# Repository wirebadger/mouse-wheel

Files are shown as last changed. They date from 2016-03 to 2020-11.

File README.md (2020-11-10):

# mouse-wheel
Arduino based exercise wheel counter for mice

# Overview
We want to see how much exercise a mouse is doing so want to count the number of revolutions on the mouse wheel.  We don't care which way the wheel is turning or how fast. In principle this is quite a simple revolution counter.

# Prototype
## Design

A magnet is glued under the wheel and every time it passes over a hall effect sensor it generates a pulse which is counted by connecting it to one of the external interrupt pins on the Arduino board.  This simple arrangement generates a lot of noisy triggers when the wheel rests with the magnet just over the sensor.  To avoid them, a second magnet is glued 180 degrees further round the wheel and a second hall effect sensor (B) is placed at 90 degrees.  Each time a magnet passes a sensor we switch to looking at the other sensor.  Every 1/4 revolution the wheel generates a signal from one of the sensors and every half turn passes sensor A and increments the count.  We are actually counting half revolutions so the result is scaled by two before display.

## Build

Glue two magnets 180 degrees apart on the wheel section.  It matters which way up they go as the sensors only detect one magnetic polarity.  

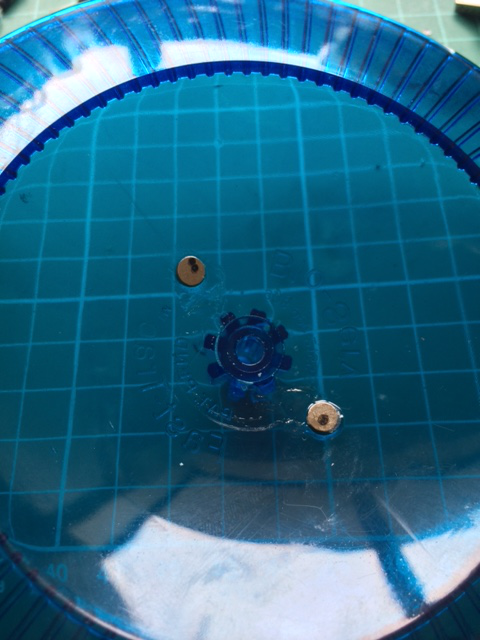
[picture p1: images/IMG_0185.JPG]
Wheel with magnets


In terms of assembly, the wheel is made of special mouse safe plastic but the rest of the wires and electronics need to be safe too.  The simplest way to get a circular PCB right up close to the wheel was to canibalise the encoder board from a small motor from [deal extreme](http://www.dx.com/p/high-torque-25mm-dc-12-0v-330rpm-encoder-precision-gear-motor-418535). 

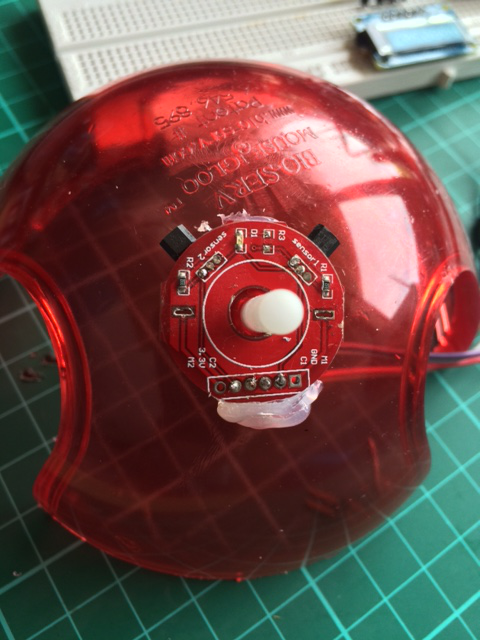
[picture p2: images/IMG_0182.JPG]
Encoder circuit


Carefully lever off the round magnet from the motor, desolder the motor pins and remove the PCB assembly. Remove the right angle connector and swap the hall effect sensors to the back  of the PCB or else the PCB doesn't fit between the wheel and the housing. Solder dupont terminated wires from the reverse side of the PCB to terminals GND, C1, C2 and VCC.  Note that this module is (probably) 3V3.  Also remove R3, the LED's resistor just to disconnect the LED and save power.  No need for disco lights.

The rest of the electronics will be housed in an aluminium enclosure and battery powered for safety. The cables running between the sensors and enclosure need to be sheathed in steel braid.

## Breadboard version
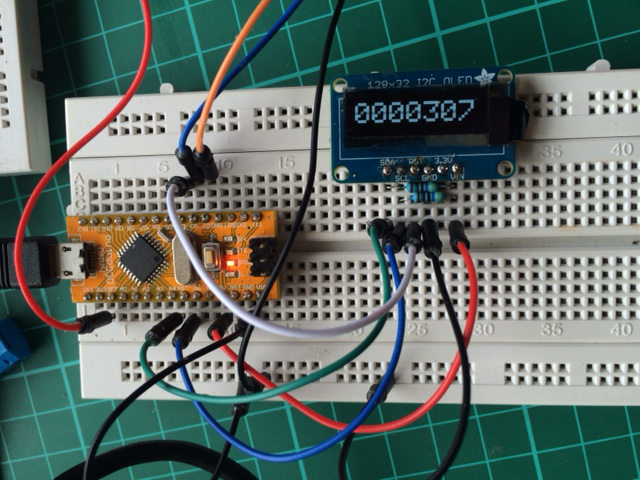
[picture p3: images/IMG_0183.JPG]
Electronics


# Results

The waveform from the two hall effect sensors can be seen below.

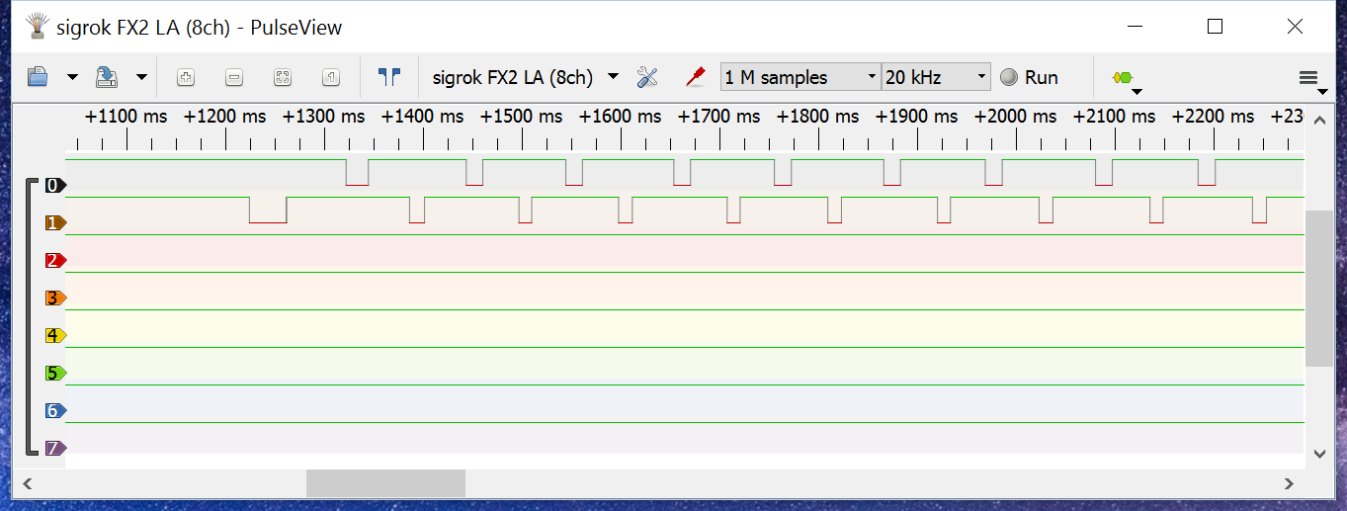
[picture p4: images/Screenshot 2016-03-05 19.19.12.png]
Outputs from both Hall Effect sensors


A falling edge on the top trace is counted only after there has been a falling edge on the second trace (brown).

If the wheel happens to stop over one of the sensors a noisy trace is generated but the addtional transitions are not counted as there is no activity on the second channel.

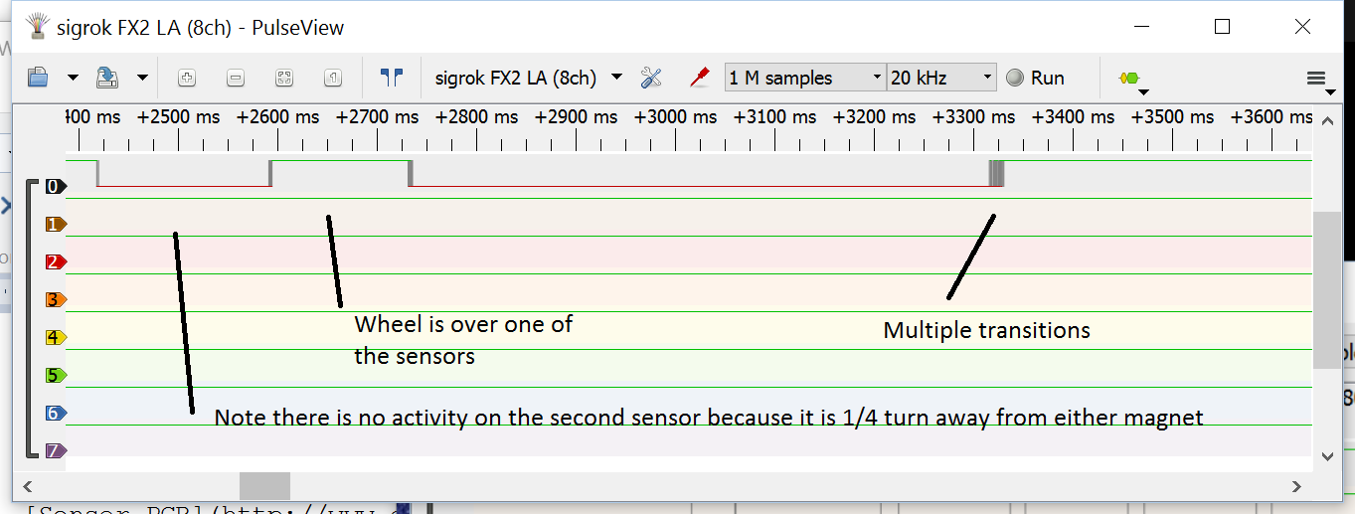
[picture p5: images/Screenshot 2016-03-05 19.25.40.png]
Wheel stops over one sensor


# First Production Build

Pro Mini connections:

|Name | Pin |Function                  |
|-----|-----|--------------------------|
|D2|5| Hall Effect sensor C1 |
|D3|6| Hall Effect sensor C2     |
|D4|7| Display Reset (active low) |
|D8|11| Wake up switch with 100k pullup to Vcc| 
|A4|-| SDA I2C line (pulled up to  Vcc with 4K7 resistor) |
|A5|-| SCL I2C line (pulled up to  Vcc with 4K7 resistor) |
|A0|17| mid point of Vraw resistor divider (2x100k) |
|Vraw|24| Unregulated supply|
|3V3|21| Supply to sensor and display|
|GND|4| Common ground |
|RXD|2| Pull high with 100k |

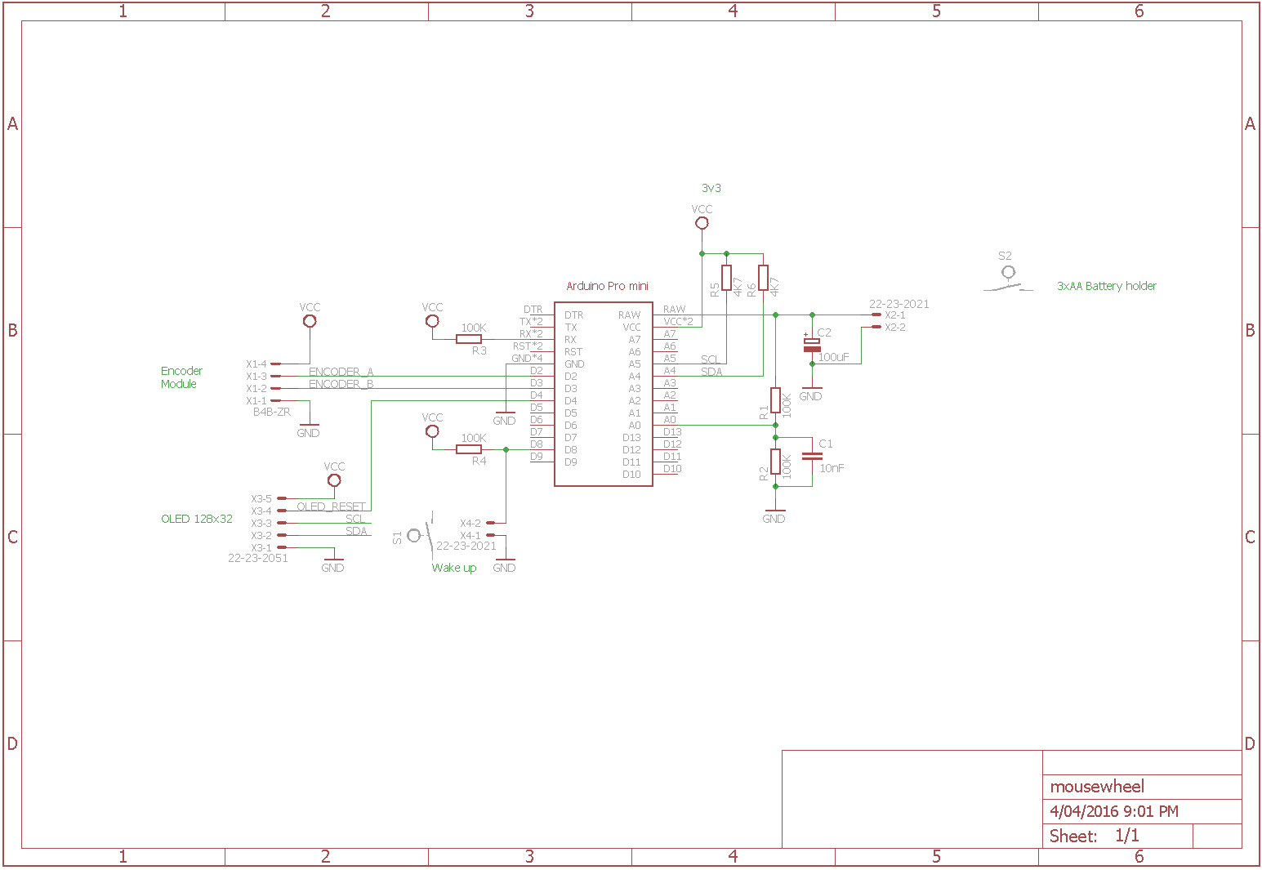
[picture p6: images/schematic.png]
Schematic


The display is the AdaFruit OLED 128x32 I2C module

## Components
### Hardware
[Display Module](https://www.adafruit.com/products/931) Adafruit OLED display

[Sensor PCB](http://www.dx.com/p/high-torque-25mm-dc-12-0v-330rpm-encoder-precision-gear-motor-418535) Removed from Motor

Was  
[Nano DCCDuino](http://www.dx.com/p/new-nano-v3-0-module-atmega328p-au-improved-version-for-arduino-yellow-369070) Set Arduino IDE for Arduino Nano

Now  
Pro Mini
Remove the LED resistor on the Pro Mini to save current

| Condition  |Ibatt typ|
|------------|---------|
|Display On  | 20mA    |
|Display Off | 4mA     |
 
### Libraries
Requires the following libraries:
* Adafruit_GFX
* Adafruit_SSD1306
* Pin Change Interrupt

Just install them using the library manager.

# Main production

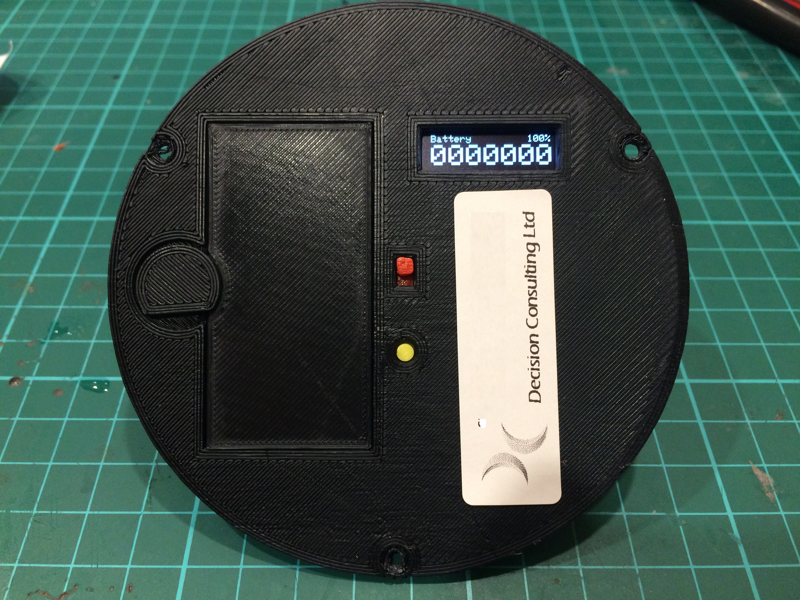
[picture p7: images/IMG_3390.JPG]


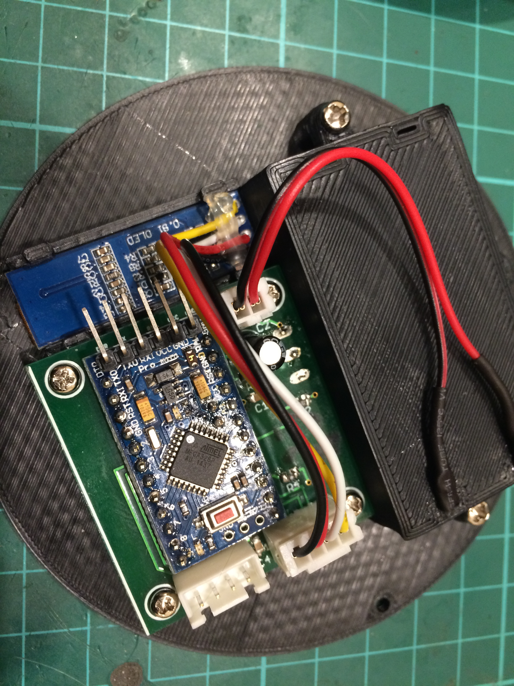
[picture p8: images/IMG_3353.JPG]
Internals


## 3D printed mechanics

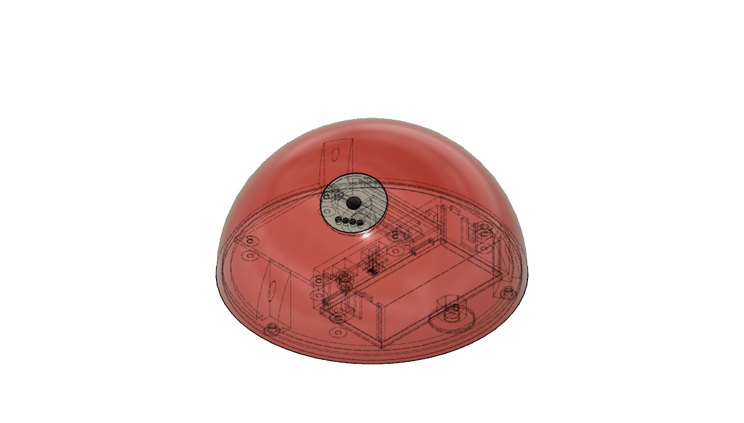
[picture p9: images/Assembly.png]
Assembly


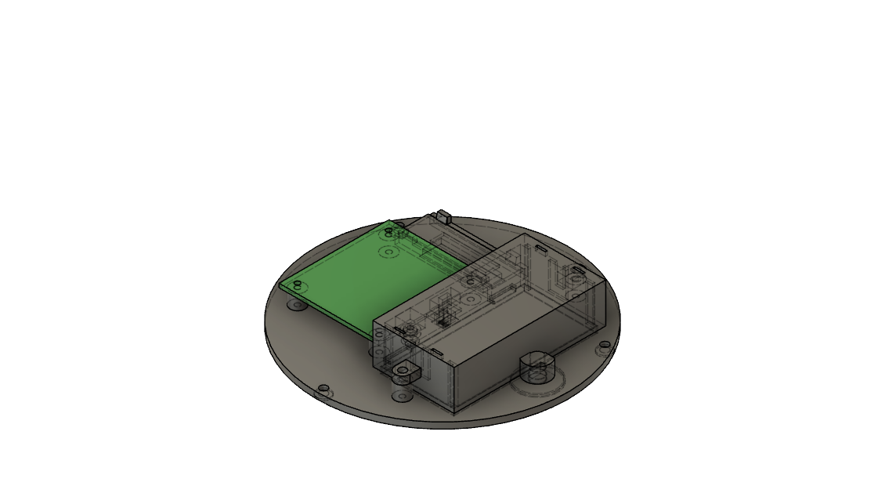
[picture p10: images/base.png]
Base


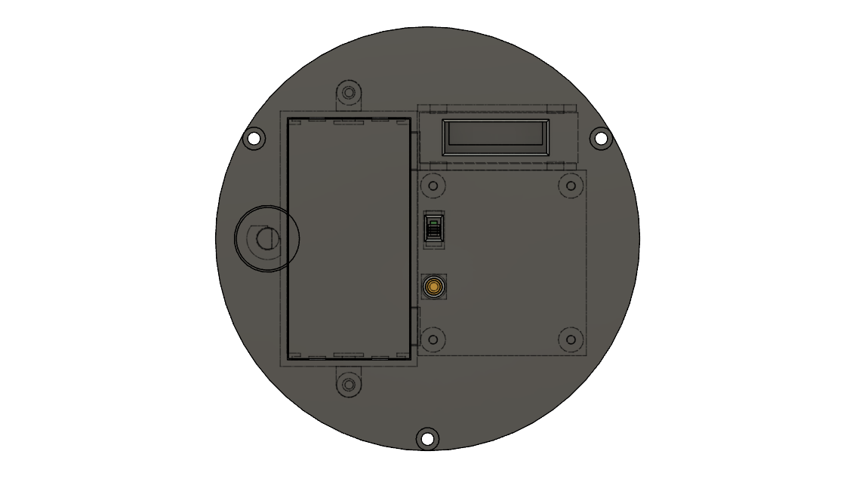
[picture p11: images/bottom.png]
Underside


See mechanical directory for design files

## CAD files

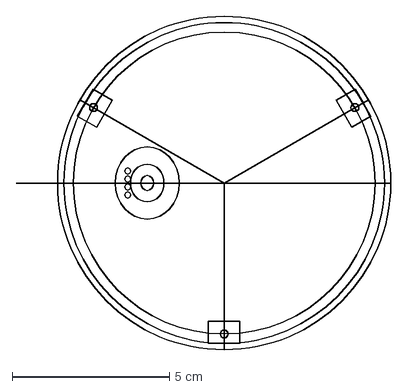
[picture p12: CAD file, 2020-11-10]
mechanical/Dome v2.dxf
11.9 x 10.6 cm

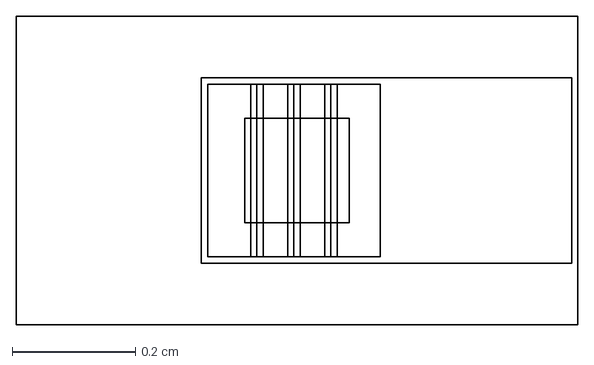
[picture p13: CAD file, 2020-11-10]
mechanical/switch.dxf
0.91 x 0.5 cm

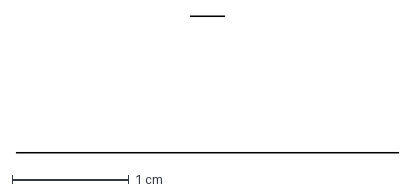
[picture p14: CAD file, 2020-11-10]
mechanical/Battery_Case_AA.dxf
3.28 x 1.17 cm

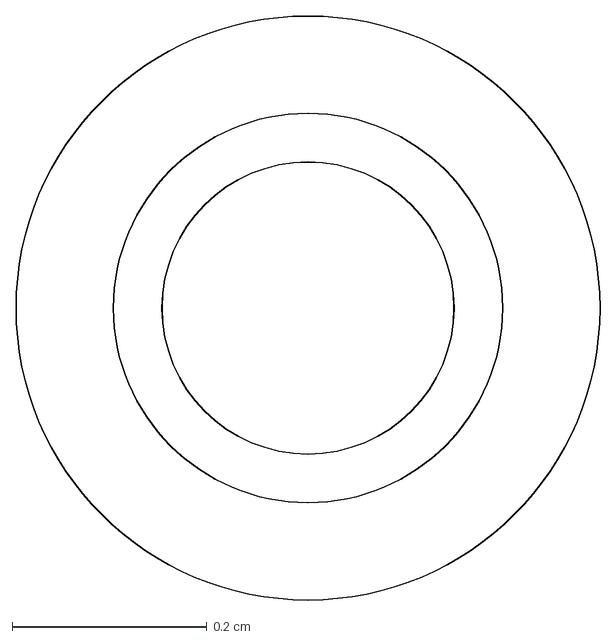
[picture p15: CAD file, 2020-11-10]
mechanical/Button.dxf
0.6 x 0.6 cm

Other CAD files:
mechanical/Assembly AA.dxf
mechanical/AA Lid.dxf
mechanical/Latch.dxf
mechanical/PCB.dxf
mechanical/Lock.dxf
mechanical/Display.dxf
mechanical/Base_AA.dxf
mechanical/Sensor PCB.dxf

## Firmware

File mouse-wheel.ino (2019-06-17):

/*! -----------------------------------------------------------------------
 * Mouse exerise wheel counter
 * Copyright [2016] Andy Dachs
 *
 * Licensed under the Apache License, Version 2.0 (the "License");
 * you may not use this file except in compliance with the License.
 * You may obtain a copy of the License at
 *
 *   http://www.apache.org/licenses/LICENSE-2.0
 *
 * Unless required by applicable law or agreed to in writing, software
 * distributed under the License is distributed on an "AS IS" BASIS,
 * WITHOUT WARRANTIES OR CONDITIONS OF ANY KIND, either express or implied.
 * See the License for the specific language governing permissions and
 * limitations under the License.
 * 
 * ------------------------------------------------------------------------
 * 
 * We want to see how exercise our mouse is doing so want to count the number of revolutions
 * on his mouse wheel.  We don't care which way the wheel is turning or how fast.
 * In principle this is quite a simple revolution counter.
 * 
 * A magnet is glued under the wheel and every time it passes over a hall effect sensor (A) it
 * generates a pulse which we can count by connecting it on of the external interrupt pins on the 
 * Arduino board.  This simple arrangement generates a lot of noisy triggers when the wheel rests 
 * with the magnet just over the sensor.  To avoid them, a second magnet is glued 180 degrees 
 * further round the wheel.  A second hall effect sensor (B) is placed at 90 degrees.  Each time 
 * a magnet passes a sensor we switch to looking at the other sensor.  Every 1/4 revolution the 
 * wheel generates a signal from one of the sensors and every half turn passes sensor A and 
 * increments the count.  We are actually counting half revolutions so the result is scaled by 
 * two before display.
 * 
 * The display is the AdaFruit OLED 128x32 I2C module
 * 
 * Requires the Adafruit_GFX and Adafruit_SSD1306. Just install them using the library manager.
 * 
 * Author: Andy Dachs
 * Date:   5th March 2016
 * 
 */

// uncomment one of these
// #define LITHIUM_1S
#define ALKALINE_2AA

// uncomment one of these
//#define LCD_128_64       // 128x64 display, i2c address 0x78/0x3C first 5 units
#define LCD_128_32       // 128x32 display, i2c address 0x78/0x3C
//#define LCD_96_16        // 0.9" narrow OLED


#include <Wire.h>
#include <Adafruit_GFX.h>
#include <Adafruit_SSD1306.h>
#include <avr/sleep.h>
#include <PinChangeInterrupt.h>


#define ENCODER_A  2          // hall effect sensor A
#define ENCODER_B  3          // quadrature hall effect sensor B
#define OLED_RESET 4          // reset pin for display module
#define WAKE_UP_SWITCH 8    // switch to wake up display
#define PIN_VBATT      A0


#ifdef LCD_96_16
#define LCDADDR     0x3C
#define LCDWIDTH    96
#define LCDHEIGHT   16 
#elif defined(LCD_128_32)
#define LCDADDR     0x3C
#define LCDWIDTH    128
#define LCDHEIGHT   32  
#elif defined(LCD_128_64)
#define LCDADDR     0x3C
#define LCDWIDTH    128
#define LCDHEIGHT   64 
#else
#error No display defined
#endif
/* Different units have different values of the resistor divider. The intention was to run from 3V but now also
 * allow for 3v7.
 * R2 47K, sometimes two in parallel 
 * R1 100K, change to 150K for LiOn
 */
#define R2                        47      //k ohms
#define R1                        150     //k ohms
#define VREF                      1100    // mV internal reference

#define VOLTAGE_SCALE             (unsigned long)(((R1+R2)*(unsigned long)VREF)/(R2))
#define VOLTAGE_HYSTERISIS        3       // mV

#ifdef ALKALINE_2AA
/* From http://www.powerstream.com/AA-tests.htm */
/* an AA battery is full at 1.45V, fully discharged at 1.1v*/
#define VBATT_FULL               (1450UL*2)   // times number of cells (below 1.45 too non-linear)
//#define VBATT_EMPTY              (1200UL*2)   // the limit is the TLE4913 hall effect Vmin 2.4V
#define VBATT_EMPTY              (1100UL*2)   // TSH253CX operates down to 1v8 so 1.1V/cell is the limit 
#define CAPACITY                 (2000UL)     // mAh
#elif defined(LITHIUM_1S)
#define VBATT_FULL               (3700UL)   
#define VBATT_EMPTY              (2900UL)    // 
#define CAPACITY                 (2600UL)    // mAh
#else
#error No Battery chemistry defined
#endif

#define REMAINING_PERCENT(mV)            ((((mV)-VBATT_EMPTY)*100)/(VBATT_FULL-VBATT_EMPTY))


#define MAX_COUNT (unsigned long)10000000

#define SERIAL_OUTPUT 1

#define DISPLAY_TIME_OUT      10000    // display timeout in ms
#define DISPLAY_REFRESH_TIME  250       // refresh display at this rate

/*! These variables must be declared volatile because they
 * are modifed in the interrupt handlers. If the main loop
 * needs to access them, interrupts must be disabled.
 */
volatile unsigned int encoder0Pos = 0;
volatile unsigned long revCount;
volatile boolean expectA;
volatile boolean displayIsActive = true;


Adafruit_SSD1306 display(LCDWIDTH, LCDHEIGHT, &Wire); //deprecated constructor display(OLED_RESET);

void doEncoderA(void);
void doEncoderB(void);
void wakeUp(void );



void setup() 
{
  pinMode(ENCODER_A, INPUT_PULLUP); 
  pinMode(ENCODER_B, INPUT_PULLUP); 

  pinMode( WAKE_UP_SWITCH, INPUT_PULLUP );
  digitalWrite( WAKE_UP_SWITCH, HIGH );

  pinMode(PIN_VBATT, INPUT);
  
  expectA = true;
  revCount = 0;

  /* Initialise OLED */
  display.begin(SSD1306_SWITCHCAPVCC, LCDADDR);  // initialize with the I2C addr
  display.clearDisplay();                            // Clear the buffer.
  display.dim(true);
    
  // encoder pin on interrupt 0 (pin 2)
  attachInterrupt(digitalPinToInterrupt(ENCODER_A), doEncoderA, FALLING);

  // encoder pin on interrupt 1 (pin 3)
  attachInterrupt(digitalPinToInterrupt(ENCODER_B), doEncoderB, FALLING);

  attachPinChangeInterrupt(digitalPinToPinChangeInterrupt(WAKE_UP_SWITCH), wakeUp, FALLING );

  disablePinChangeInterrupt(digitalPinToPinChangeInterrupt(WAKE_UP_SWITCH));

  // serial output
#if SERIAL_OUTPUT
  Serial.begin (115200);
#endif

  analogReference( INTERNAL );   // 1.1v internal reference
}


void loop()
{
  unsigned long count;
  unsigned long newRevs;
  uint8_t oldSFR;
  static unsigned long oldRevs = -1;
  static unsigned long displayOnTime = 0;
  static unsigned long displayRefreshTime = 0;
  static unsigned int voldbatt = 0;
  unsigned long timeNow = millis();

  /* disable interrupts so we can safely read and modify variables */
  oldSFR = SREG;
  cli();
  count = revCount;
  if( count >= (2*MAX_COUNT) )
    revCount = 0;
  SREG = oldSFR;

  /* we count half revolutions */
  newRevs = count/2;

  if( (timeNow - displayRefreshTime > DISPLAY_REFRESH_TIME) && displayIsActive)
  {
    display.clearDisplay();
    display.setCursor(1,1);
    display.setTextSize(1);
    display.setTextColor(WHITE);
    
    display.print( "Battery" );
    unsigned int vbatt = (analogRead( PIN_VBATT ) * VOLTAGE_SCALE)/1024;
      
    display.setCursor(100,1);
    if( vbatt < VBATT_EMPTY )
      vbatt = VBATT_EMPTY;
    if( abs(vbatt - voldbatt) > VOLTAGE_HYSTERISIS )
    {
      voldbatt = vbatt;
    }
    unsigned int percent = REMAINING_PERCENT(voldbatt);
    if ( percent > 100 )
      percent = 100;
    display.print( percent );
    display.print("% ");
    

    oldRevs = newRevs;
    display.setCursor(1,11);
    display.setTextSize(3);
    display.setTextColor(WHITE);

    /* display count with leading zeros */
    unsigned long position = MAX_COUNT/10;
    do
    {
      unsigned int digit = (newRevs / position) % 10;
      display.print( digit );
      position /= 10;
#if SERIAL_OUTPUT
      Serial.print( digit );
#endif
    } while( position > 0 );
    
        
#if SERIAL_OUTPUT
    Serial.println();
#endif

    display.display();
    displayRefreshTime = timeNow;
      
  }
  

  if( (timeNow - displayOnTime > DISPLAY_TIME_OUT ) && displayIsActive )
  {
    oldSFR = SREG;
    cli();
    displayIsActive = false;
    SREG = oldSFR;
    
    display.ssd1306_command( SSD1306_DISPLAYOFF );
  }

  if( !displayIsActive )
  {
    // enable pin change interrupt
    sleep_enable();  
    enablePinChangeInterrupt(digitalPinToPinChangeInterrupt(WAKE_UP_SWITCH));
    set_sleep_mode( SLEEP_MODE_PWR_DOWN );
    sleep_mode();
  
    // execute from here on wakeup
    sleep_disable();
  
  
    if( displayIsActive )
    {
      disablePinChangeInterrupt(digitalPinToPinChangeInterrupt(WAKE_UP_SWITCH));
      displayOnTime = millis();
      display.ssd1306_command( SSD1306_DISPLAYON );
    }
  }
}

/*! 
 * Interrupt on A changing state
 */
void doEncoderA(){
  /* ignore any interrupts we're not expecting */
  if( expectA )
  {
    expectA = false;
    revCount++;
  }
  sleep_disable();
}

/*! 
 * Interrupt on B changing state
 */
void doEncoderB(){
  if( !expectA )
  {
    expectA = true;
  }
  sleep_disable();
}

void wakeUp(void)
{
  sleep_disable();
//  detachPCINT(WAKE_UP_SWITCH);
//  disablePinChangeInterrupt(digitalPinToPinChangeInterrupt(WAKE_UP_SWITCH));
  displayIsActive = true;
}

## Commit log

2016-03-05 Rename .ino to keep arduino ide happy
2016-03-12 Add power save modes and switch to Pro Mini
2016-03-12 Use Pin Change Interrupt Library
2016-03-13 Add battery level indicator
2016-03-17 Add hysterisis to battery measurement to avoid flickering
2019-06-05 Modify low votlage point for TSH253 sensors
2019-06-17 Fix integer scaling problem with voltage reading
2020-11-10 Add images of production units + Fusion 360 files
    [AA Lid.dxf, Assembly AA.dxf, Base_AA.dxf, Battery_Case_AA.dxf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]
